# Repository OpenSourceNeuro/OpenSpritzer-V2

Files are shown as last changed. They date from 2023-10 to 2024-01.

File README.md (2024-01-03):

<p align="left">
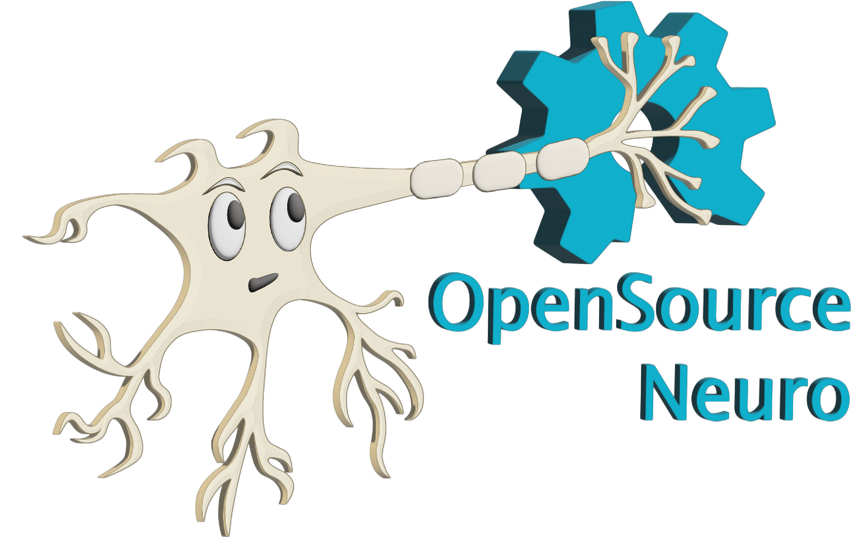
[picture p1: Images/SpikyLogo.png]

</p>

<h1 align="center"> OpenSpritzer v2</h1>
<h3 align="center">  An Open hardware pressure ejection system for reliably delivering picolitre volumes.</h3></p>
<h6 align="right">developed by M.J.Y. Zimmermann</h6>

<br></br>

This project is licensed under the <a href="https://www.gnu.org/licenses/gpl-3.0.html">GNU General Public License v3.0</a>
<br>
The hardware is licensed under the <a href="https://cern-ohl.web.cern.ch">CERN OHL v1.2</a>

***

<div align= "justify">

<p>
Designed for ease of use, robustness and low-cost, the “Openspritzer” is an open hardware “Picospritzer” as routinely used in biological labs around the world. The performance of Openspritzer and commercial alternatives is effectively indistiguishable.
</p>

<p>
The system is based on a solenoid valve connected to a pressure gauge. Control can be attained directly via an external TTL pulse or internally through an Arduino set by a rotary encoder. The basic setup can be put together for ~400€, or substantially less if you are prepare to shop around.
</p>

<p>
We anticipate that due to its high performance and low cost Openspritzer will be of interest to a broad range of researchers working in the life and physical sciences.
</p>

<br>

</div>

<p align="center">
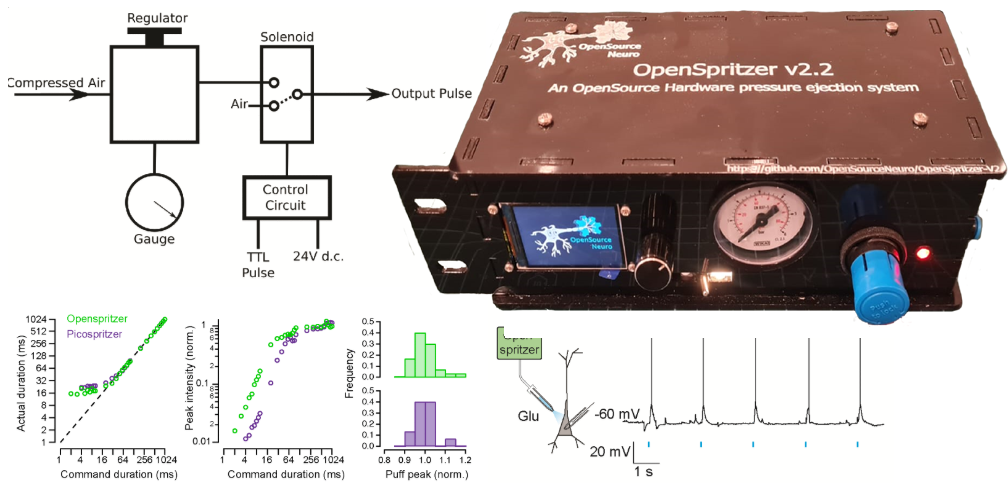
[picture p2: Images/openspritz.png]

</p>

<p align= "right">
The original work was published in <a href="https://www.nature.com/articles/s41598-017-02301-2"> Forman et al. 2017, Scientific Reports</a>
</p>

***

<h2 align="left">
OpenSpritzer, a DIY open source micro-injector:
</h2>

<br>

<div align= "justify">

<p>
Compared to similar commercial systems that can cost up to several thousand pounds, the cost of the fully equipped Openspritzer (~£300) makes it particularly attractive for those wishing to pursue cutting-edge techniques in low resource environments.
</p>

<p>
This repository contains detailed <a href="https://github.com/OpenSourceNeuro/OpenSpritzer-V2/blob/main/Installation_Manual.md">assembly instructions and an operation manual</a> for OpenSpritzer. The <a href="https://github.com/OpenSourceNeuro/OpenSpritzer-V2/blob/main/BOM.csv">bill of material</a> details all pneumatic, mechanical and electronic components required.
</p>

<p>
To simplify the wiring assembly, a customed circuit board has been designed. PCB prototype companies (i.e. <a href="jlcpcb.com"> JLCPCB</a>) will only require the <a href="https://github.com/OpenSourceNeuro/OpenSpritzer-V2/tree/main/PCB_Rack%20version"> gerber.zip</a> folder to be sent to them for production.
</p>

<br></br>

</div>

***

<h2 align="left">
Openspritzer rivals the performance of commercial systems:
</h2>

<br>

<div align= "justify">

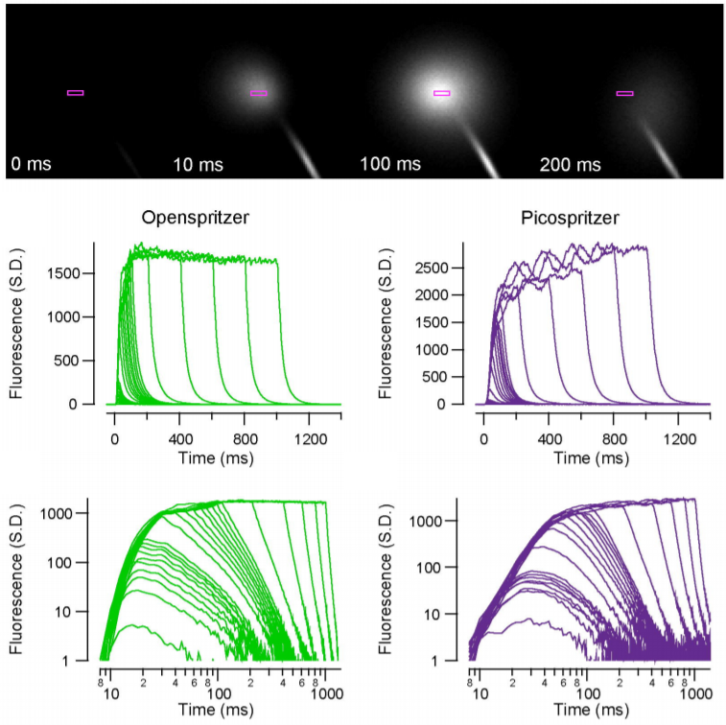
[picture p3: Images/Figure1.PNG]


<p>
Openspritzer control over dose delivery matches that of a leading commercial alternative.
</p>

<p>
To directly assess the time precision and reliability of Openspritzer we visualised fluorescent dye puffs from a sharp microelectrode under two-photon microscopy. The images were taken from a puff with a duration of several seconds using a wide area scan (rectangles).
</p>

<p>
Fluorescence profiles of different command-duration puffs are shown for Openspritzer (green) and Picospritzer, a popular microinjection system(purple), respectively. The same data is shown again in log-log space to highlight details of shorter pulses. Overall, both devices behave in a very similar way in terms of providing effective and near linear control over the total dosage.
</p>

<br></br>

</div>

***

<h2 align="left">
OpenSpritzer in neuroscience experiments:
</h2>

<br>

<div align= "justify">

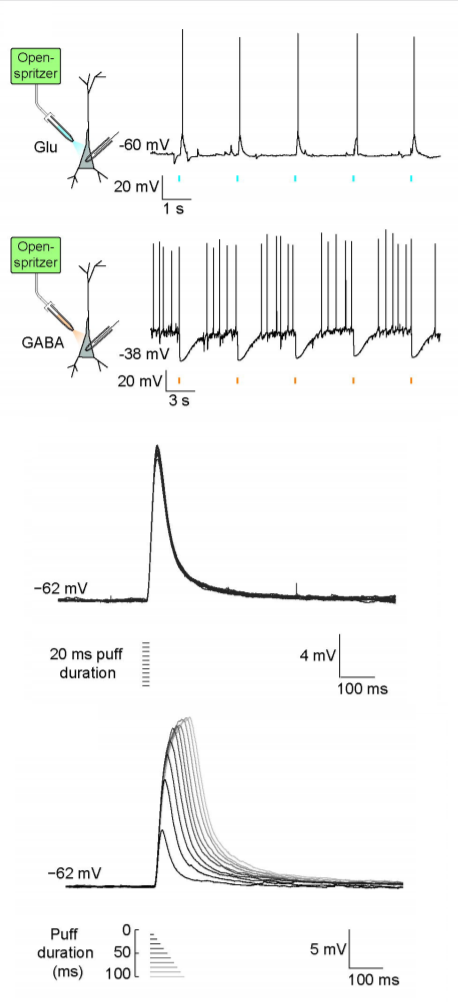
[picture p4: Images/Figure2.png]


<p>
Openspritzer controls neural activity by delivering neurotransmitters with millisecond precision.
</p>

<p>
To demonstrate the utility of Openspritzer, we use it in a series of standard neurobiological applications: We delivered precise amounts of glutamate(cyan) and GABA(orange) to hippocampal neurons to elicit time- and dose-precise excitatory and inhibitory responses respectively, while monitoring the voltage response of the recorded neuron in current-clamp mode.
</p>

<p>
20 ms doses of glutamate (100 μM) reliably evoked excitatory postsynaptic potentials (EPSPs) and action potentials. Similarly, action potential activity elicited via somatic current injection could be suppressed by 20 ms puffs of GABA (100 μM).
</p>

<p>
To assess the accuracy of the drug delivery, we applied 10 sweeps where a 20 ms glutamate puff was applied after 500 ms produced almost identical EPSPs demonstrating the precise timing of Openspritzer and highly conserved puff volumes.
</p>

<p>
Then, to test the effect of command duration on effective dose delivey, we next applied puffs of increasing duration from 10 to 100 ms in 10 ms steps. Here, each additional 10 ms increase in duration produced a clear increase in both EPSP duration and amplitude. These results confirm the reliability and precision of Openspritzer for delivering small doses of an agent to a widely used biological sample in a controlled manner.
</p>

<br></br>

</div>

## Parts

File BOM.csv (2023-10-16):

Name | Manufacturer | Order ID | Retailer | Retailer ID | Quantity |  |  | Observation
Solenoid | FESTO | MHJ10-S-2,5-QS-6-HF | RS | 175-2145 | 1 | https://fr.rs-online.com/web/p/electrodistributeurs/1752145 | 92.35 | Pneumatics
Precision pressure regulator | FESTO | MS2-LR-QS6-D6-A8-B | RS | 204-0052 | 1 | https://fr.rs-online.com/web/p/regulateurs-de-pression/2040052 | 30.38 | Pneumatics
Gauge | WIKA | 30810876 | RS | 222-7480 | 1 | https://fr.rs-online.com/web/p/manometres/2227480 | 11.52 | Pneumatics
6mm air tubing | FESTO | PEN-6XT-NT | RS | 126-2781 | 1 |  |  | Pneumatics
PicoNozzle Kit | World Precision Instrument | 5430 - x | WPI |  | 1 |  |  | Pneumatics
ESP32 -devkit 32 | Espressif | ESP32-DEVKITC-32E | DigiKey | 1965-ESP32-DEVKITC-32E-ND | 1 | https://www.digikey.fr/fr/products/detail/espressif-systems/ESP32-DEVKITC-32E/12091810 | 9.3 | Electronics
2 inch LCD display module ST7789 | Waveshare
PCB socket | Samtec | SSW-116-02-G-S | RS |  | 2 |  |  | Electronics
NPN transistor | onsemi | KSP 2222 ABU | RS | 739-0385 | 3 | https://fr.rs-online.com/web/p/transistors-bipolaires/7390385?gb=s | 3.18 | Electronics
Rotary Encoder |  | KY-040 |  |  | 1 |  | 1.5 | Electronics
Knob for rotary encoder |  |  |  |  | 1 |  |  | Electronics
DPDT switch | nkk switches | B22AH | DigiKey | 360-3752-ND | 1 |  | 6.2 | Electronics
SPST footswitch | RS Pro | 808-6989 | RS | 808-6989 | 1 |  | 33.78 | Electronics
24V DC PSU 2.1 mm jack | RS Pro | 436-058 | RS | 436-058 | 1 |  | 25 | Electronics
2.1 mm right angle DC socket | RS Pro | 884-0957 | RS | 884-0957 | 1 |  | 1.87 | Electronics
24 V Zener Diode | STMicroelectronics | 1N5822 | RS | 687-0877 | 1 |  |  | Electronics
1 kOhm resistor | Digikey | CF14JT1K00CT-ND | Digikey |  | 1 |  |  | Electronics
2 kOhm resistor | Digikey | CF14JT2K00CT-ND | Digikey |  | 1 |  |  | Electronics
220 Ohm resistor | Digikey | CF14JT220RCT-ND | Digikey |  | 3 |  |  | Electronics
Voltage step-down regulator | RS Pro | LM2596T-5.0 NOPB | RS | 533-3743 | 1 |  | 6.62 | Electronics
Capacitor 680 µF | RS Pro | 526-1569 | RS | 526-1569 | 1 |  | 1.06 | Electronics
Capacitor 220 µF | RS Online | 526-1480 | RS | 526-1480 | 1 |  | 0.58 | Electronics
Inductor 33 µH | Wurth Elektronik | 744772330 | RS | 489-0059 | 1 |  |  | Electronics
3 mm LED (white preferably ) | Digikey | 350-1557-ND | Digikey |  | 3 |  |  | Electronics
Mount for 3 mm LED | Digikey | 67-1330-ND | Digikey |  | 1 |  |  | Electronics
BNC coaxial connectors | RS PRO | 546-5115 | RS | 546-5115 | 2 |  |  | Electronics
Cable Mount BNC Connector | RS PRO | 546-3721 | RS | 546-3721 | 1 |  |  | Electronics
2 way JST Female Connector Housing | JST | XHP-2 | RS | 820-1611 | 1 |  |  | Electronics
3 way JST Female Connector Housing | JST | XHP-3 | RS | 820-1614 | 2 |  |  | Electronics
8 way JST Female Connector Housing | JST | XHP-8 | RS | 820-1633 |  |  |  | Electronics
2 way JST PCB header | JST | B2B-XH | RS | 820-1554 | 1 |  |  | Electronics
3 way JST PCB header | JST | B3B-XH | RS | 820-1557 | 2 |  |  | Electronics
8 way JST PCB header | JST | B8B-XH | RS | 820-1576 |  |  |  | Electronics
Rocker LED switch |  | BRockerB-XH | Ebay |  | 1 |  |  | Electronics

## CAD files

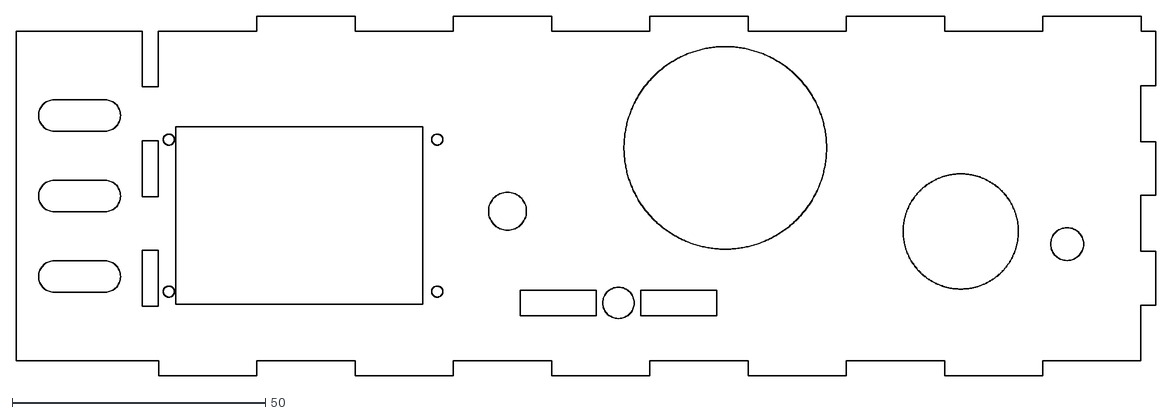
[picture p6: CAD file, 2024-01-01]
Casing/front.dxf
225.0 x 71.0

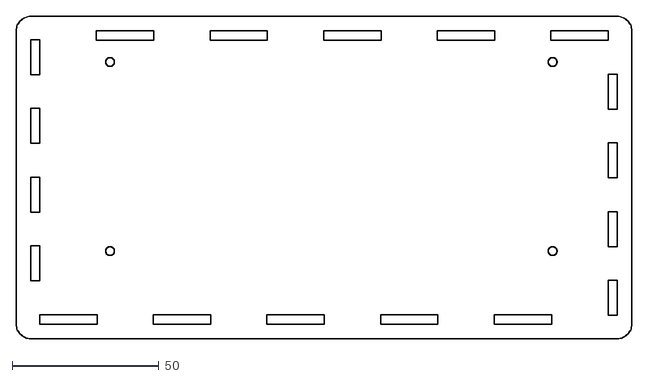
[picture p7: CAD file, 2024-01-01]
Casing/Rack_mount/bottom.dxf
210.0 x 110.0

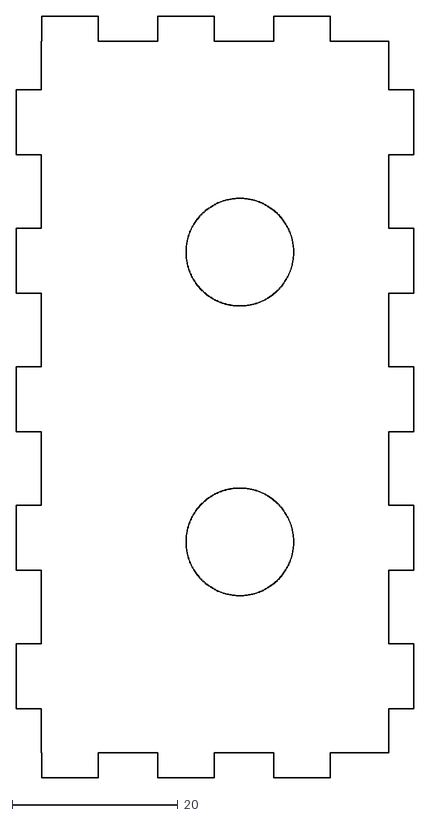
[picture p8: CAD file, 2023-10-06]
Casing/left.dxf
48.0 x 92.0

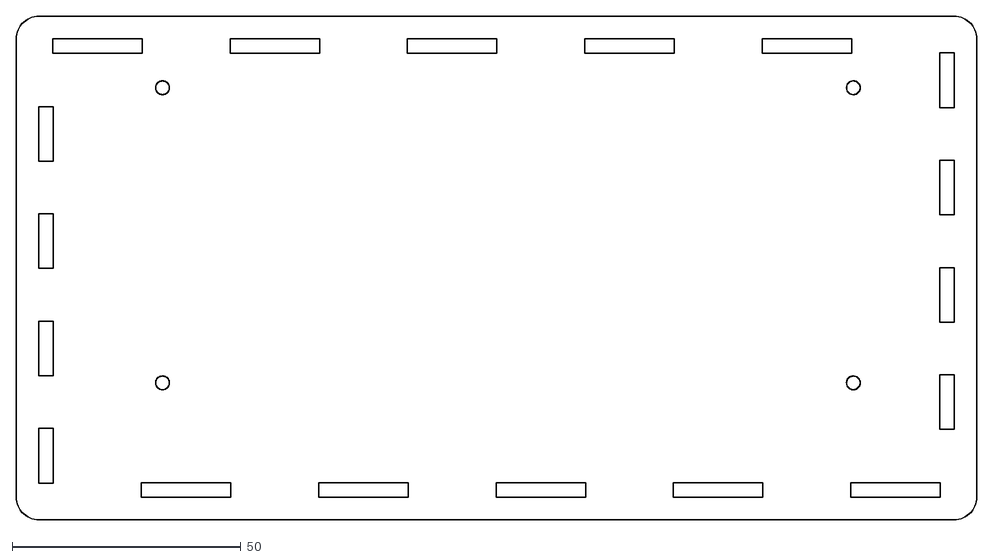
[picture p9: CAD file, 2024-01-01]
Casing/Rack_mount/top.dxf
210.0 x 110.0

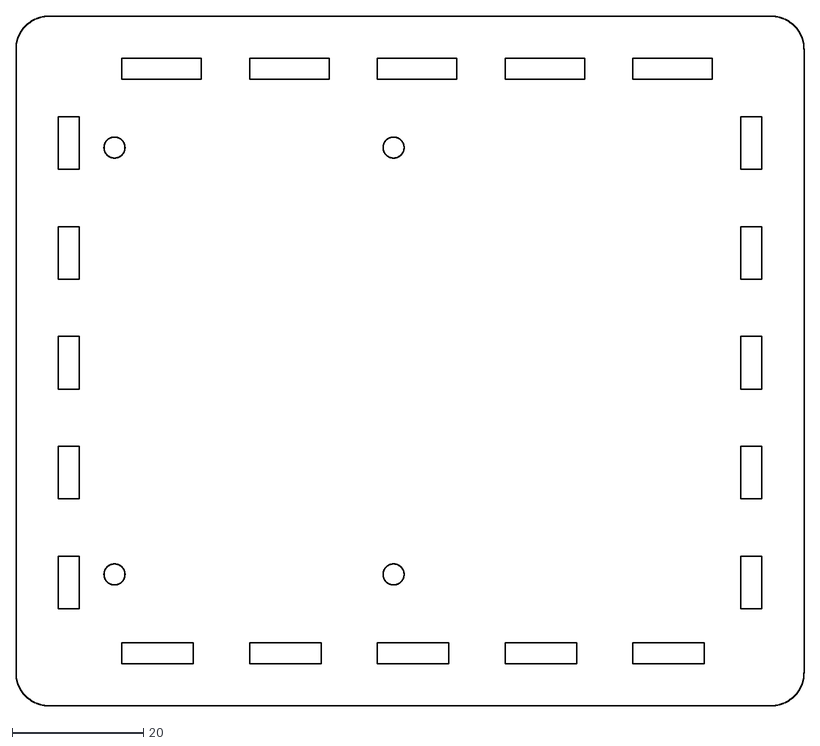
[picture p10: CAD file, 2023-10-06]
Casing/bottom.dxf
120.0 x 105.0

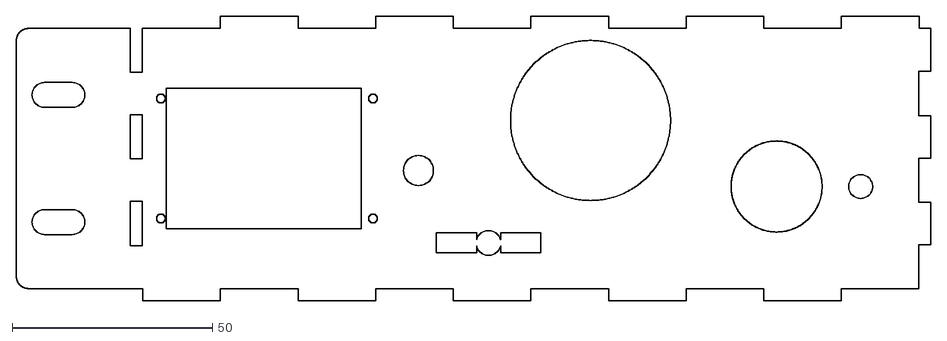
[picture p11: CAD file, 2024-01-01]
Casing/Rack_mount/front.dxf
228.5 x 71.0

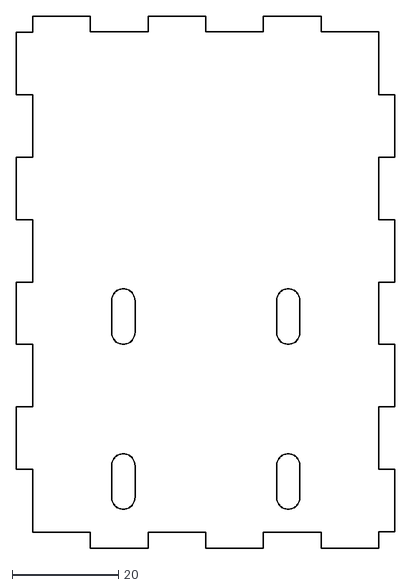
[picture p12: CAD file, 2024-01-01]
Casing/Rack_mount/left.dxf
71.1 x 100.0

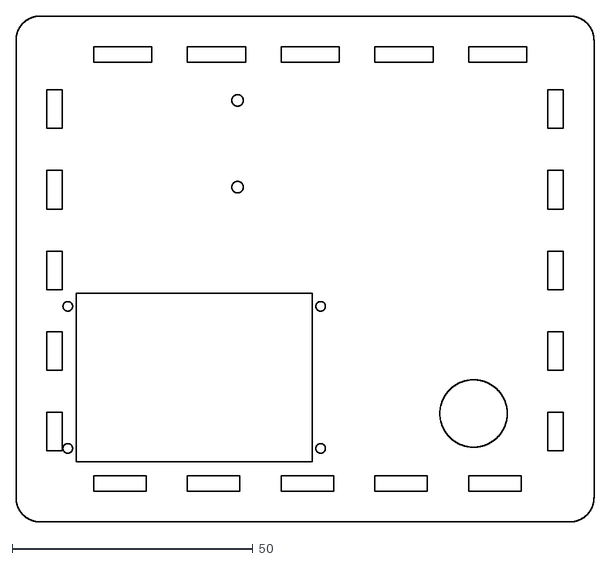
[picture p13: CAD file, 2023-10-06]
Casing/top.dxf
120.0 x 105.0

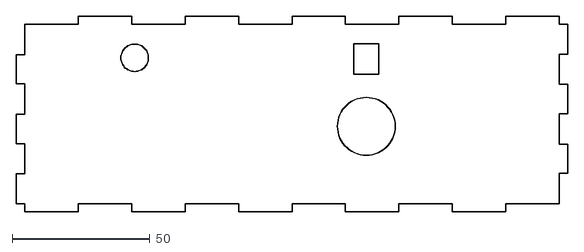
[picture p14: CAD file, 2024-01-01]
Casing/Rack_mount/back.dxf
200.0 x 71.0

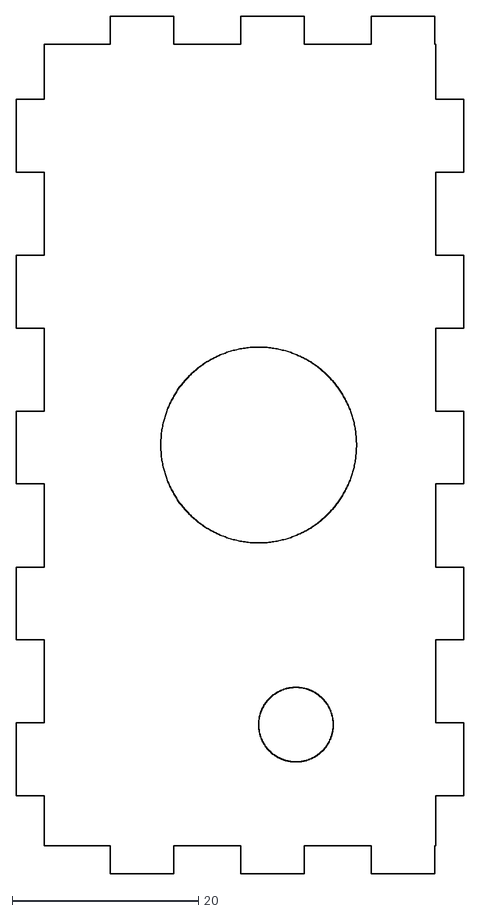
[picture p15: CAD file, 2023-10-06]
Casing/right.dxf
48.0 x 92.0

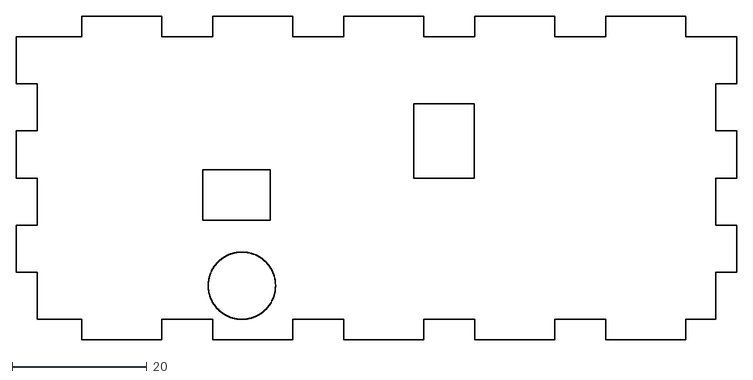
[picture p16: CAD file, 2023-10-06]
Casing/back.dxf
107.0 x 48.0

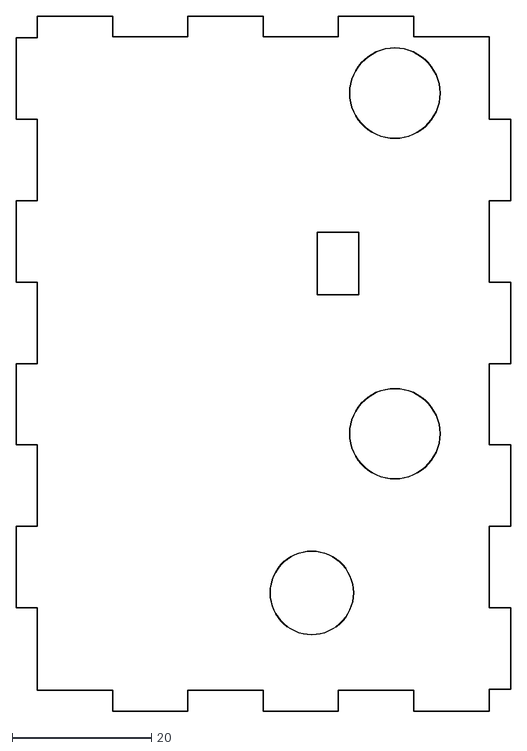
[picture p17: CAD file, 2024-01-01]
Casing/Rack_mount/right.dxf
71.1 x 100.0

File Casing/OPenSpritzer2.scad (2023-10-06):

Acrylic_Wall = 3;
tol = 0.1;
Smoothness = 60;
xxx = 20;


x_PCB = 65;
y_PCB = 85;
z_PCB = 2;
r_PCB = 3;
r_Acrylic = 5;

PCB_Spacing = 2.54;

r_hex = 5.65/2;
hex_bottom = 8;
hex_top = 20+8;



// // // Switches // // //
DXF = 0;

PCB = 1;

BNC90 = 10;
DPDT = 10;
Power = 10;
ESP = 10;
Rotary = 10;

Regulator = 1;
Solenoid = 1;

Hex_Bottom = 1;
Hex_Top = 1;

Acrylic_Bottom  = 1;
Acrylic_Top  = 1;
Acrylic_Front  = 1;
Acrylic_Back  = 1;
Acrylic_Left  = 1;
Acrylic_Right  = 1;

// // // Parameters // // // //

x_BNC90 = 14.8;
y_BNC90 = 14.9;
z_BNC90 = 13.1;
h1_BNC90 = 10.5;
r1_BNC90 = 12.8/2;
h2_BNC90 = 9.8;
r2_BNC90 = 9.6/2;
h_pinBNC90 = 4.2;
r_pinBNC90 = 0.89/2;
offset_pinBNC90 = 0.2;

x_ESP = 55;
y_ESP = 28;
z_ESP = 11.5;
x_USB = 6;
y_USB = 9;
z_USB = 6;
h_USB = 3;
xpos_ESP = 4.3;
ypos_ESP = 0;
r_pinUSB = 0.6/2;
h_pinUSB = 5;

x_Power = 9;
y_Power = 13.6;
z_Power = 11;
xoffset_pinPower1 = 25;
yoffset_pinPower1 = y_PCB - 4.75;
xoffset_pinPower2 = 20.3;
yoffset_pinPower2 = y_PCB - 7.79;
xoffset_pinPower3 = 25;
yoffset_pinPower3 = y_PCB - 10.8;
x_pinPower1 = 4.5;
y_pinPower1 = y_Power-7.5;
x_pinPower2 = -0.1;
y_pinPower2 = y_Power-10.8;
x_pinPower3 = 4.5;
y_pinPower3 = y_Power-13.6;
xpos_Power = 60;
ypos_Power = y_PCB-4.75;

x_Switch = 8.8;
y_Switch = 13.7;
z_Switch = 8.8;
r_Switch = 6/2;
h_Switch = 2.7;
hpos_Switch = 4.4;
xoffset_pinSwitch = 1.86;
yoffset_pinSwitch = 7.62;
h_pinSwitch = 4.2;
r_pinSwitch = 0.6/2;
xoffset_pinSwitch1 = 25;
xoffset_pinSwitch2 = 25+PCB_Spacing;
xoffset_pinSwitch3 = 25-PCB_Spacing;
xoffset_pinSwitch4 = 50;
xoffset_pinSwitch5 = 50+PCB_Spacing;
xoffset_pinSwitch6 = 50-PCB_Spacing;
yoffset_pinSwitch1 = y_PCB-88.07;
yoffset_pinSwitch2 = y_PCB-90.62;

xpos1_M3 = 5;
xpos2_M3 = 47.5;
ypos1_M3 = 10;
ypos2_M3 = 75;
r_M3 = 3/2;

r_Hole = 0.5+tol;
ypos_BNC90_1 = y_PCB-60;
ypos_BNC90_1bis = y_PCB-82.54;
ypos_BNC90_2 = y_PCB-25;
ypos_BNC90_2bis = y_PCB-22.5;
xpos_BNC90 = 12.4;
xpos_Switch_1 = 24;
xpos_Switch_1bis = 27.7;
ypos_Switch = y_PCB-80.75;

xpos_Rotary = 47.5;
ypos_Rotary = 1.5;
zpos_Rotary = 22;
r_Rotary = 7.5/2;
h_Rotary = 25;

xmargin_Acrylic = 10;
ymargin_Acrylic = 10;
x_Acrylic = x_PCB + 2*xmargin_Acrylic;
y_Acrylic = y_PCB + 2*ymargin_Acrylic;
z_Acrylic = Acrylic_Wall;

x_AcrylicFront = x_PCB;
y_AcrylicFront = Acrylic_Wall;
z_AcrylicFront = z_PCB + hex_bottom + hex_top ;

x_AcrylicSide = Acrylic_Wall;
y_AcrylicSide = y_PCB;
z_AcrylicSide = z_PCB + hex_bottom + hex_top;

y1margin_AcrylicFront = 2;
y2margin_AcrylicFront = 2;

x1margin_AcrylicSide = 2;
x2margin_AcrylicSide = 2;
x1margin_AcrylicFront = x1margin_AcrylicSide+Acrylic_Wall;
x2margin_AcrylicFront = x2margin_AcrylicSide+Acrylic_Wall;

y1margin_AcrylicSide = y1margin_AcrylicFront;
y2margin_AcrylicSide = y2margin_AcrylicFront;




// // // Functions // // //

if (PCB == 1){
    difference(){
        PCB();
        translate([xpos1_M3,ypos1_M3,-tol])cylinder(r=r_M3,h=z_PCB+2*tol,$fn=Smoothness);
        translate([xpos1_M3,ypos2_M3,-tol])cylinder(r=r_M3,h=z_PCB+2*tol,$fn=Smoothness);
        translate([xpos2_M3,ypos1_M3,-tol])cylinder(r=r_M3,h=z_PCB+2*tol,$fn=Smoothness);
        translate([xpos2_M3,ypos2_M3,-tol])cylinder(r=r_M3,h=z_PCB+2*tol,$fn=Smoothness);
    }
}

if (Rotary == 1){
    Rotary();
}


module Rotary(){
    translate([xpos_Rotary,ypos_Rotary,zpos_Rotary])rotate([90,0,0])cylinder(r=r_Rotary,h=h_Rotary,$fn=Smoothness);
}

if (BNC90 == 1){
    translate([xpos_BNC90,ypos_BNC90_1,0])BNC90();
    translate([xpos_BNC90,ypos_BNC90_2,0])BNC90();
}

if (ESP == 1){
    translate([14.8,y_PCB-0.25,z_PCB])rotate([0,0,-90])ESP();
}

if (Power == 1){
    translate([xpos_Power,ypos_Power,0])Power();
}

if (DPDT == 1){
    translate([xpos_Switch_1,ypos_Switch,0])Switch();
}

if (Hex_Bottom == 1){
    translate([xpos1_M3,ypos1_M3,-hex_bottom])Hex(hex_bottom);
    translate([xpos2_M3,ypos1_M3,-hex_bottom])Hex(hex_bottom);
    translate([xpos1_M3,ypos2_M3,-hex_bottom])Hex(hex_bottom);
    translate([xpos2_M3,ypos2_M3,-hex_bottom])Hex(hex_bottom);
}

if (Hex_Top == 1){
    translate([xpos1_M3,ypos1_M3,z_PCB])Hex(hex_top);
    translate([xpos2_M3,ypos1_M3,z_PCB])Hex(hex_top);
    translate([xpos1_M3,ypos2_M3,z_PCB])Hex(hex_top);
    translate([xpos2_M3,ypos2_M3,z_PCB])Hex(hex_top);
}

if (Regulator == 1){
    translate([90,28,15])rotate([0,0,0])Regulator();
}

if (Solenoid == 1){
    translate([52.5,y_PCB-30,z_PCB+hex_top-10-tol])rotate([0,0,0])Solenoid();
}

if (Acrylic_Bottom == 1 && DXF == 0){
    Acrylic_Botom();
}
if (Acrylic_Bottom == 1 && DXF == 1){
    Acrylic_Botom_DXF();
}


if (Acrylic_Top == 1 && DXF == 0){
    Acrylic_Top();
}
if (Acrylic_Top == 1 && DXF == 1){
    Acrylic_Top_DXF();
}


if (Acrylic_Front == 1 && DXF == 0){
    Acrylic_Front();
}
if (Acrylic_Front == 1 && DXF == 1){
    Acrylic_Front_DXF();
}


if (Acrylic_Back == 1 && DXF == 0){
    Acrylic_Back();
}
if (Acrylic_Back == 1 && DXF == 1){
    Acrylic_Back_DXF();
}


if (Acrylic_Left == 1 && DXF == 0){
    Acrylic_Left();
}
if (Acrylic_Left == 1 && DXF == 1){
    Acrylic_Left_DXF();
}


if (Acrylic_Right == 1 && DXF == 0){
    Acrylic_Right();
}
if (Acrylic_Right == 1 && DXF == 1){
    Acrylic_Right_DXF();
}


// // // Modules // // //


module PCB(){
    color([0.1,0.8,0])translate([r_PCB,r_PCB,0])minkowski(){
        cube([x_PCB-2*r_PCB,y_PCB-2*r_PCB,z_PCB-tol]);
        cylinder(r=r_PCB,h=tol,$fn=Smoothness);
    }
}

module BNC90(){
    color([1,1,1])translate([-x_BNC90+offset_pinBNC90+r_pinBNC90,-y_BNC90/2,z_PCB])cube([x_BNC90,y_BNC90,z_BNC90]);
    color([1,1,1])translate([-x_BNC90+offset_pinBNC90+r_pinBNC90-h1_BNC90,0,z_BNC90/2+z_PCB])rotate([0,90,0])cylinder(r=r1_BNC90+tol,h=h1_BNC90,$fn=Smoothness);
    color([192/255,192/255,192/255])translate([-x_BNC90+offset_pinBNC90+r_pinBNC90-h1_BNC90-h2_BNC90,0,z_BNC90/2+z_PCB])rotate([0,90,0])cylinder(r=r2_BNC90,h=h2_BNC90,$fn=Smoothness);
    translate([0,0,-h_pinBNC90+z_PCB])cylinder(r=r_pinBNC90,h=h_pinBNC90,$fn=Smoothness);
    translate([0,-PCB_Spacing,-h_pinBNC90+z_PCB])cylinder(r=r_pinBNC90,h=h_pinBNC90,$fn=Smoothness);
}

module Power(){
    color([0.1,0.1,0.1])translate([-x_pinPower1,-y_pinPower1,z_PCB]){
        cube([x_Power,y_Power+xxx,z_Power]);
        translate([x_pinPower1,y_pinPower1,-tol-z_PCB])cylinder(r=r_Hole,h=z_PCB+2*tol,$fn=Smoothness);
        translate([x_pinPower2,y_pinPower2,-tol-z_PCB])cylinder(r=r_Hole,h=z_PCB+2*tol,$fn=Smoothness);
        translate([x_pinPower3,y_pinPower3,-tol-z_PCB])cylinder(r=r_Hole,h=z_PCB+2*tol,$fn=Smoothness);
    }
}

module Switch(){
    translate([-xoffset_pinSwitch,-y_Switch+yoffset_pinSwitch,z_PCB]){
        color([0.8,0.1,0.1])cube([x_Switch,y_Switch,z_Switch]);
        color([192/255,192/255,192/255])translate([x_Switch/2,0,hpos_Switch])rotate([90,0,0])cylinder(r=r_Switch+tol,h=h_Switch+xxx,$fn=Smoothness);
        translate([xoffset_pinSwitch,y_Switch-yoffset_pinSwitch,-h_pinSwitch+z_PCB])cylinder(r=r_pinSwitch,h=h_pinSwitch,$fn=Smoothness);
        translate([x_Switch-xoffset_pinSwitch,y_Switch-yoffset_pinSwitch,-h_pinSwitch+z_PCB])cylinder(r=r_pinSwitch,h=h_pinSwitch,$fn=Smoothness);
        translate([xoffset_pinSwitch,y_Switch-yoffset_pinSwitch+2*PCB_Spacing,-h_pinSwitch+z_PCB])cylinder(r=r_pinSwitch,h=h_pinSwitch,$fn=Smoothness);
        translate([xoffset_pinSwitch+PCB_Spacing,y_Switch-yoffset_pinSwitch+2*PCB_Spacing,-h_pinSwitch+z_PCB])cylinder(r=r_pinSwitch,h=h_pinSwitch,$fn=Smoothness);
        translate([xoffset_pinSwitch+2*PCB_Spacing,y_Switch-yoffset_pinSwitch+2*PCB_Spacing,-h_pinSwitch+z_PCB])cylinder(r=r_pinSwitch,h=h_pinSwitch,$fn=Smoothness);
        translate([xoffset_pinSwitch,y_Switch-yoffset_pinSwitch+3*PCB_Spacing,-h_pinSwitch+z_PCB])cylinder(r=r_pinSwitch,h=h_pinSwitch,$fn=Smoothness);
        translate([xoffset_pinSwitch+PCB_Spacing,y_Switch-yoffset_pinSwitch+3*PCB_Spacing,-h_pinSwitch+z_PCB])cylinder(r=r_pinSwitch,h=h_pinSwitch,$fn=Smoothness);
        translate([xoffset_pinSwitch+2*PCB_Spacing,y_Switch-yoffset_pinSwitch+3*PCB_Spacing,-h_pinSwitch+z_PCB])cylinder(r=r_pinSwitch,h=h_pinSwitch,$fn=Smoothness);
    }
}

module Hex(height){
    color([255/255,215/255,0])cylinder(r=r_hex,h=height,$fn=8);
}

module ESP(){
    translate([-xpos_ESP,ypos_ESP,z_PCB]){cube([x_ESP,y_ESP,z_ESP]);
        translate([-xxx,y_ESP/2-y_USB/2,z_ESP+h_USB-z_USB/2])cube([x_USB+xxx,y_USB,z_USB]);
    }  
}
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

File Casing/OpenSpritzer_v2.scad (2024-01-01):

Wall = 3;
tol = 0.1;
Smoothness = 360;
Sm = 60;
Acrylic = [0,0,0.8,0.8];

// // // // // // // // // // // // // //
// // // // //   Switches  // // // // //

DXF = 1;

PCB = 10;
BNC90 = 10;
DPDT = 10;
Power = 10;
Power_Switch = 10;
ESP = 10;
Rotary = 10;
Festo = 10;

Regulator = 10;
Manometer = 10;
Solenoid = 10;
Screen = 10;

Hex_Bottom = 10;
Hex_Top = 10;

Rack19 = 10;

Acrylic_Bottom  = 10;
Acrylic_Top  = 10;
Acrylic_Front  = 10;
Acrylic_Back  = 10;
Acrylic_Left  = 1;
Acrylic_Right  = 10;


// // // // // // // // // // // // // //
// // // // General Settings  // // // //

r_hex = 5.65/2;
hex_bottom = 5;
hex_top = 18+20+20;
z_PCB = 2;

x_Box = 200;
y_Box = 100;
z_Box = hex_bottom + z_PCB + hex_top;
r_Box = 5;

x_PCB = 180;
y_PCB = y_Box-2*Wall-2*tol;
r_PCB = 3;

r_Rack = 3+tol;
x_Rack = 25.5;
x_rack = 7;
x_rack_minus = 5-1;
x_rack_plus = x_rack+x_rack_minus;
d_Rack = 15.9;


xpos1_M3 = x_Box-Wall-x_PCB+10;
xpos2_M3 = x_Box-Wall-x_PCB+161;
ypos1_M3 = y_Box-Wall-tol-72;
ypos2_M3 = y_Box-Wall-tol-7.5;
r_M3 = 3/2;




    x_Rack19 = 25;
    y_Rack19 = 2;
    z_Rack19 = 44.45;
    
    X_Rack19 = 2;
    Y_Rack19 = 45;
    Z_Rack19 = 44.45;
    
    d_Rack19 = 13;
    D_Rack19 = 31;
    l_Rack19 = 14.5;
    r_Rack19 = 4/2+0.2;
    R_Rack19 = 7/2;
    L_Rack19 = 6;
    dd_Rack19 = 25+2*R_Rack19;
    ypos1 = 8;
    ypos2 = 17;
    ypos3 = 30;
    ypos4 = 39;
    xpos1 = 6;
    xpos2 = 12;

// // // // // // // // // // // // // //
// // // // //  Functions  // // // // //

if (PCB == 1){
    translate([x_Box-x_PCB-Wall-tol,Wall+tol,Wall+hex_bottom])difference(){
        PCB();
        translate([32,y_PCB-7.1,-20])cylinder(r=1.3,h=100,$fn=60);
        translate([32,y_PCB-25.1,-20])cylinder(r=1.3,h=100,$fn=60);
    }
}




if (BNC90 == 1){
    BNC90();
}

if (ESP == 1){
    ESP();
}

if (Power == 1){
    Power();
}

if (Power_Switch == 1){
    Power_Switch();
}

if (DPDT == 1){
    Switch();
}

if (Hex_Bottom == 1){
    translate([xpos1_M3,ypos1_M3,Wall])Hex(hex_bottom);
    translate([xpos2_M3,ypos1_M3,Wall])Hex(hex_bottom);
    translate([xpos1_M3,ypos2_M3,Wall])Hex(hex_bottom);
    translate([xpos2_M3,ypos2_M3,Wall])Hex(hex_bottom);
}

if (Hex_Top == 1){
    translate([xpos1_M3,ypos1_M3,Wall+hex_bottom+z_PCB])Hex(hex_top);
    translate([xpos2_M3,ypos1_M3,Wall+hex_bottom+z_PCB])Hex(hex_top);
    translate([xpos1_M3,ypos2_M3,Wall+hex_bottom+z_PCB])Hex(hex_top);
    translate([xpos2_M3,ypos2_M3,Wall+hex_bottom+z_PCB])Hex(hex_top);
}

if (Festo == 1){
    Festo();
}
if (Regulator == 1){
    Regulator();
}
if (Manometer == 1){
    Manometer();
}

if (Solenoid == 1){
    Solenoid();
}

if (Screen == 1){
    Screen();
}
if (Rotary == 1){
    Rotary();
}
if  (Rack19 == 1){
    Rack19();
}


if (Acrylic_Bottom == 1 && DXF == 0){
    Acrylic_Botom();
}
if (Acrylic_Bottom == 1 && DXF == 1){
    Acrylic_Botom_DXF();
}


if (Acrylic_Top == 1 && DXF == 0){
    Acrylic_Top();
}
if (Acrylic_Top == 1 && DXF == 1){
    Acrylic_Top_DXF();
}


if (Acrylic_Front == 1 && DXF == 0){
    Acrylic_Front();
}
if (Acrylic_Front == 1 && DXF == 1){
    Acrylic_Front_DXF();
}


if (Acrylic_Back == 1 && DXF == 0){
    Acrylic_Back();
}
if (Acrylic_Back == 1 && DXF == 1){
    Acrylic_Back_DXF();
}


if (Acrylic_Left == 1 && DXF == 0){
    Acrylic_Left();
}
if (Acrylic_Left == 1 && DXF == 1){
    Acrylic_Left_DXF();
}


if (Acrylic_Right == 1 && DXF == 0){
    Acrylic_Right();
}
if (Acrylic_Right == 1 && DXF == 1){
    Acrylic_Right_DXF();
}


// // // // // // // // // // // // // //
// // // // //   Modules   // // // // //

module PCB(){
    color([0.1,0.8,0])translate([r_PCB,r_PCB,0])minkowski(){
        cube([x_PCB-2*r_PCB,y_PCB-2*r_PCB,z_PCB-tol]);
        cylinder(r=r_PCB,h=tol,$fn=Smoothness);
    }
}

module Rotary(){
r_Rotary = 7.5/2;
h_Rotary = 25;
x_Rotary = 19;
y_Rotary = 26;
z_Rotary = 1;
    translate([x_Box-x_PCB-Wall+55,12.5,Wall+hex_bottom+z_PCB+22.5])rotate([90,0,0]){
        cylinder(r=r_Rotary,h=h_Rotary,$fn=Sm);
        translate([-11.25,-y_Rotary+10,0])cube([x_Rotary,y_Rotary,z_Rotary]);
    }
}



module BNC90(){
x_BNC90 = 14.8;
y_BNC90 = 14.9;
z_BNC90 = 13.1;
h1_BNC90 = 10.5;
r1_BNC90 = 12.8/2;
h2_BNC90 = 9.8;
r2_BNC90 = 9.6/2;
h_pinBNC90 = 4.2;
r_pinBNC90 = 0.89/2;
offset_pinBNC90 = 0.2;
    translate([x_Box-Wall-14,Wall+tol+y_PCB-57,Wall+hex_bottom])rotate([0,0,180])BNC();
    translate([x_Box-Wall-14,Wall+tol+y_PCB-8   ,Wall+hex_bottom])rotate([0,0,180])BNC();
    
    module BNC(){
        color([1,1,1])translate([-x_BNC90+offset_pinBNC90+r_pinBNC90,-y_BNC90/2,z_PCB])cube([x_BNC90,y_BNC90,z_BNC90]);
        color([1,1,1])translate([-x_BNC90+offset_pinBNC90+r_pinBNC90-h1_BNC90,0,z_BNC90/2+z_PCB])rotate([0,90,0])cylinder(r=r1_BNC90+tol,h=h1_BNC90,$fn=Sm);
        color([192/255,192/255,192/255])translate([-x_BNC90+offset_pinBNC90+r_pinBNC90-h1_BNC90-h2_BNC90,0,z_BNC90/2+z_PCB])rotate([0,90,0])cylinder(r=r2_BNC90,h=h2_BNC90,$fn=Sm);
        translate([0,0,-h_pinBNC90+z_PCB])cylinder(r=r_pinBNC90,h=h_pinBNC90,$fn=Sm);
        translate([0,-2.54,-h_pinBNC90+z_PCB])cylinder(r=r_pinBNC90,h=h_pinBNC90,$fn=Sm);
    }
}

module Power(){
x_Power = 9;
y_Power = 13.6;
z_Power = 11;
 
    color([0.1,0.1,0.1])translate([x_Box-x_PCB-Wall+110,y_Box-13,Wall+hex_bottom+z_PCB]){
        translate([-x_Power/2,0,0])cube([x_Power,y_Power,z_Power]);
    }
}

module Power_Switch(){
x_Power = 9;
y_Power = 13.6;
z_Power = 11;
r_Power = 21/2;

    
    color([0.1,0.1,0.1])translate([x_Box-x_PCB-Wall+110+x_Power/2,y_Box-Wall-tol,Wall+hex_bottom+z_PCB]){
        translate([-x_Power/2,0,30])rotate([-90,0,0])cylinder(r=r_Power, h=Wall+2*tol, $fn=Sm);
    }
}

module Switch(){
x_Switch = 8.8;
y_Switch = 13.7;
z_Switch = 8.8;
r_Switch = 6/2;
h_Switch = 2.7+5;    
hpos_Switch = 4.4;
    translate([x_Box-x_PCB-Wall+72.5,Wall+tol,Wall+hex_bottom+z_PCB]){
        color([0.8,0.1,0.1])cube([x_Switch,y_Switch,z_Switch]);
        color([192/255,192/255,192/255])translate([0,0,hpos_Switch])rotate([90,0,0])cylinder(r=r_Switch+tol,h=h_Switch,$fn=Sm);
    }
}

module Panels(){
x_Panel = 10;
z_Panel = 5;
r_Switch = 6/2;
hpos_Panel = 4.4-z_Panel/2;

    translate([x_Box-x_PCB-Wall+72.5+r_Switch,-tol,Wall+hex_bottom+z_PCB+hpos_Panel])cube([x_Panel, Wall+2*tol,z_Panel]);
    translate([x_Box-x_PCB-Wall+72.5-x_Panel-r_Switch,-tol,Wall+hex_bottom+z_PCB+hpos_Panel])cube([x_Panel, Wall+2*tol,z_Panel]);
}

module Hex(height){
    color([255/255,215/255,0])cylinder(r=r_hex,h=height,$fn=8);
}

module ESP(){
x_ESP = 55;
y_ESP = 28;
z_ESP = 11.5;
x_USB = 6;
y_USB = 9;
z_USB = 6;
h_USB = 3;
xpos_ESP = 4.3;
ypos_ESP = 0;
r_pinUSB = 0.6/2;
h_pinUSB = 5;
    translate([x_Box-Wall-tol-3.25,14+Wall+tol+y_PCB-32.5,Wall+hex_bottom+z_PCB-1.75])rotate([0,0,180]){
        translate([-xpos_ESP,ypos_ESP,z_PCB]){
            cube([x_ESP,y_ESP,z_ESP]);
            translate([-Wall-tol,y_ESP/2-y_USB/2,z_ESP+h_USB-z_USB/2])cube([x_USB+Wall+tol,y_USB,z_USB]);
        }  
    }
}

module Festo(){
    color([1,0,1])translate([x_Box-12.5,17,Wall+hex_bottom+Wall+17.5])rotate([0,90,0])cylinder(r=12/2,h=25,$fn=Sm);
}

module Regulator(){
    reg_r_base = 27/2;
    reg_h_base = 6.5;
    reg_x = 27;
    reg_y = 25;
    reg_z = 22;
    reg_r_top = 26/2;
    reg_h_top = 3;
    reg_thread_r = 22.75/2;
    reg_thread_h = 7;
    reg_ring_r = 21.5/2;
    reg_ring_h = 4;
    reg_gauge_r = 14/2;
    reg_gauge_h = 2;
    reg_gauge2_h = 5.5;
    reg_gauge2_x = 14+1.1;
    reg_gauge2_z = 5;
    reg_tube_r = 6/2+1;
    reg_tube_h = 50;
    reg_gauge_screw = 22.5/2;
    translate([x_Box-38.5,31.5+Wall,Wall+hex_bottom+Wall+17.5])color([1,0,1])rotate([90,0,0]){
        cylinder(r=reg_r_base,reg_h_base,$fn=Smoothness);
        translate([-reg_x/2,-reg_y/2,reg_h_base])cube([reg_x,reg_y,reg_z]); 
        translate([0,0,reg_h_base+reg_z])cylinder(r=reg_r_top,reg_h_top,$fn=Smoothness);
        translate([0,0,reg_h_base+reg_z+reg_h_top])cylinder(r=reg_thread_r,reg_thread_h,$fn=Smoothness);
        translate([0,0,reg_h_base+reg_z+reg_h_top+reg_thread_h])cylinder(r=reg_ring_r,reg_ring_h,$fn=Smoothness);
        translate([0,-reg_y/2,reg_h_base+reg_z/2])rotate([90,0,0])cylinder(r=reg_gauge_r,h=reg_gauge_h,$fn=Smoothness);
        translate([0,reg_y/2+reg_gauge_h,reg_h_base+reg_z/2])rotate([90,0,0])cylinder(r=reg_gauge_r,h=reg_gauge_h,$fn=Smoothness);
        
        translate([-reg_x/2,0,reg_h_base+reg_z/2])rotate([0,90,0])cylinder(r=reg_tube_r,h=reg_tube_h,$fn=Smoothness);
        translate([reg_y/2,0,reg_h_base+reg_z/2])rotate([0,-90,0])cylinder(r=reg_tube_r,h=reg_tube_h,$fn=Smoothness);        
    }
}  

module Spritzer_LED(){
r_LED = 6/2;
    
    translate([x_Box-17.5,-tol,Wall+hex_bottom+Wall+17.5])rotate([-90,0,0])cylinder(r=r_LED,h=Wall+2*tol,$fn=Sm);
}
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

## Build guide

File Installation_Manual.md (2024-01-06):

<p align="left">

</p>

<h1 align="center"> OpenSpritzer v2 - Installation Manual</h1></p>

<br></br>

<h2 align="left">
Overview
</h2>

<br>

<div align= "justify">

<p>
This document contains detailed assembly instructions, a software guideline and includes a parts list.
</p>

<p>
The Arduino code and 3D casing files (SCAD) for either 3D printing or laser cutting (STL and DXF) can be downloaded <a href="https://github.com/OpenSourceNeuro/OpenSpritzer-V2/tree/main/Casing"><strong>here</strong></a>, and further modified to fit customise purposes. The device is designed to regulate the pressure and duration of a single or repeated puff(s) of compressed air. Typically, the output air port is connected to a glass puffer pipette which has been drawn into a sharp point with a narrow (2-3μm) diameter pore.
</p>

<p>
The device itself consists of a printed circuit board, a microcontroller, a solenoid valve, a pressure regulator with a manometer and various interface, off-the-shelf, components.
</p>

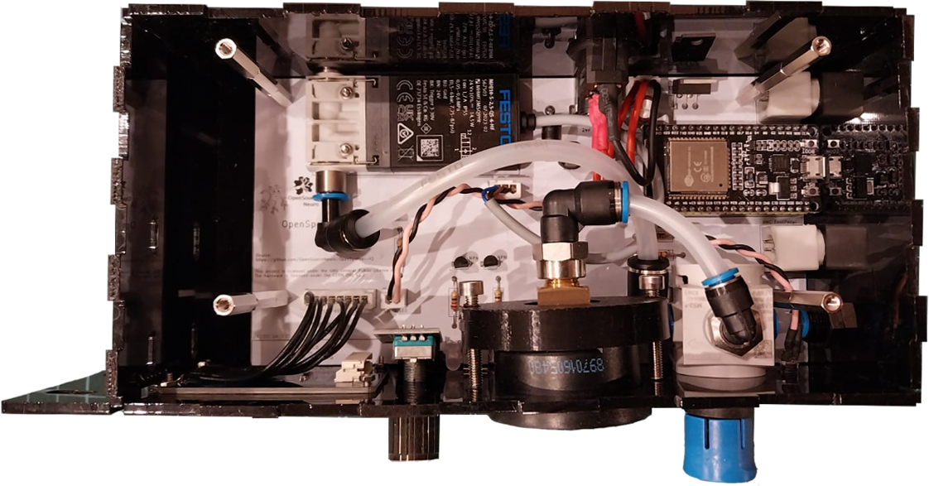
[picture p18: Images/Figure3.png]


<p>
The device is here shown without its covering lid.
The pressure regulator is mounted on the right and attached to the front panel via a retaining threaded ring that comes with the regulator.
M3 threaded spacers are mounted onto the PCB and are meant to be screwed to the top and bottom part of the box.
The solenoid is screwed directly onto the PCB.
The manometer is locked onto the front panel with a 3D printed part and two M3 bolts.
</p>

</div>

<br></br>

## Driver Installation
<br>

OpenSpritzer firmware runs on an Espressif ESP32 board and requires the USB to UART bridge <a href="https://www.silabs.com/developers/usb-to-uart-bridge-vcp-drivers"> CP210x driver</a>,  which can be downloaded<a href="https://www.silabs.com/developers/usb-to-uart-bridge-vcp-drivers?tab=downloads"> <strong>here</strong></a>.

Once the driver has been installed, users can upload and modify the <a href="https://github.com/OpenSourceNeuro/OpenSpritzer-V2/tree/main/Arduino/OpenSpritzer_V2">microcontroller code</a> through the <a href="https://www.arduino.cc/en/software">Arduino IDE</a> (Integrated Development Environment).

<br></br>

## Microcontroller Arduino code

<br>

##### Arduino IDE

<br>

The ESP32 microcontroller runs a C++ code which can be accessed via the Arduino IDE, which can be downloaded <a href="https://www.arduino.cc/en/software">here</a>.

<br>

##### ESP32 Add-on

<br>

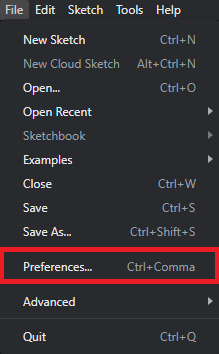
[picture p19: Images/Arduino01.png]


Once the IDE is installed, users needs to install the ESP32 board library:

In the Arduino IDE, go to <strong> File > Preferences </strong>

Enter the following link into the <strong>Additional Board Manager URLs</strong> field:

https://raw.githubusercontent.com/espressif/arduino-esp32/gh-pages/package_esp32_index.json

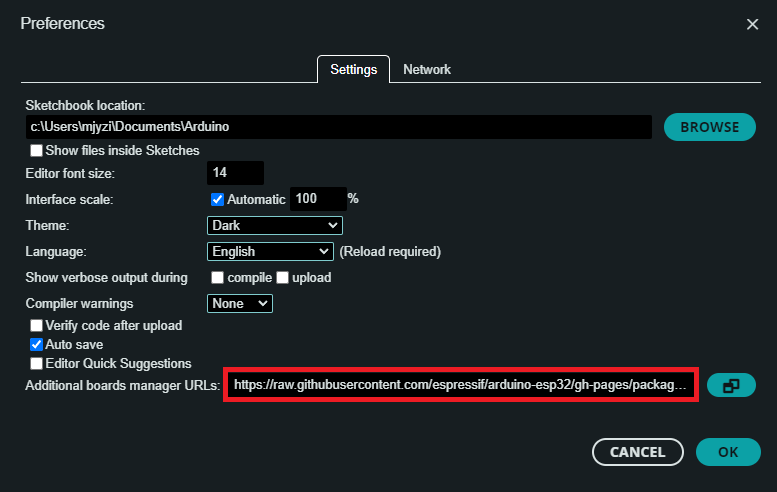
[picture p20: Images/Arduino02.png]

Then click on the <strong>OK</strong> button.

<br></br>

Next, open the Boards Manager. Go to <strong> Tools > Board > Board Manager...</strong>

Search for ESP32 and press install button for the <strong>ESP32 by Espressif Systems</strong>.

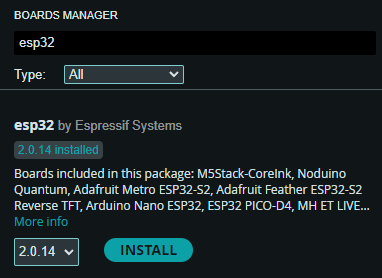
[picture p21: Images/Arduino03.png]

Then click on the <strong>Install</strong> button.

<br></br>

##### Compiling the code

<br>

Within the Arduino IDE, user needs to select the FQBN (Fully Qualified Board Name) on which the code will be compiled for.

Here the ESP32 Dev Module needs to be selected.

Go to <strong>Tools > Board > esp32 > ESP32 Dev Module </strong>


The board name should be displayed  as shown.

<br></br>

Before compiling the LED Zappelin code, a few librairies need to be installed:
  - Arduino-SerialCommand
  - Adafruit_TLC5947
  - Adafruit_NeoPixel

Most of them can be downloaded from the Arduino IDE: Go to <strong>Sketch > Include Librairy > Manage Libraries</strong>, enter the library name, then install it following the same process as for the board library.

We however recommend for the Arduino-SerialCommand library to manually place the library folder which can be found <a href="https://github.com/OpenSourceNeuro/LED-Zappelin-V2/tree/main/Arduino/Librairies">here</a> into the library folder. For Windows Users: <strong>C:/Users/x/Documents/Arduino/libraries</strong>

Now everything is set to compile and verify the code.

Users can now select the COM port on which the ESP32 is connected ( Go to <strong>Tools > port</strong> ) and upload the code onto the board.

<br></br>

##### Code and calibration

<br>

The code runs continuously on the board in a loop detailed in the main tab (LED_Zappelin_V2.ino).
To not interfere with the proper function and communication of the program, avoid modifying this part of the code.

<br>

In <strong>General_Settings.h</strong>:

- There exists two versions for the NeoPixel strips that serve as proxy LEDs for the device. If the proxy LEDs do not display the appropriate colours, comment/uncomment the Adafruit_NeoPixel functions:


<br>

In <strong> LED_Values.h </strong>

- Users can select here the colours displayed by the proxy LEDs by entering the wavelength corresponding to each stimulating LEDs.


- The TLC5947 is a linear current-sink LED driver with a 12bits resolution (4096 values).
However, some LEDs may reach their maximum intensities before reaching the maximum stimulating value (4095). A calibration step is then require here.

    Trimmer potentiometers corresponding to each LED channels can be found on the device. They regulate the maximum current intensity each stimulating LED can be drove with.

    First, user need to set each stimulating LED to their desired maximum intensity by adjusting the potentiometer value.

    Once done, play a <a href="">step-increased stimulation sequence</a> for the tested LED and not at which value the LED maximum intensity is reached and (may?) plateau.

    Finally enter the noted value in the <strong> LED_Values.h</strong> tab.
    

    <br></br>

    Reupload the code onto the board, now the tested LED will have a linear intensity increase from 0 to 100% without any saturation.

<br></br>

No further modification of the code is then required from the user who can now control the board directly from the GUI.

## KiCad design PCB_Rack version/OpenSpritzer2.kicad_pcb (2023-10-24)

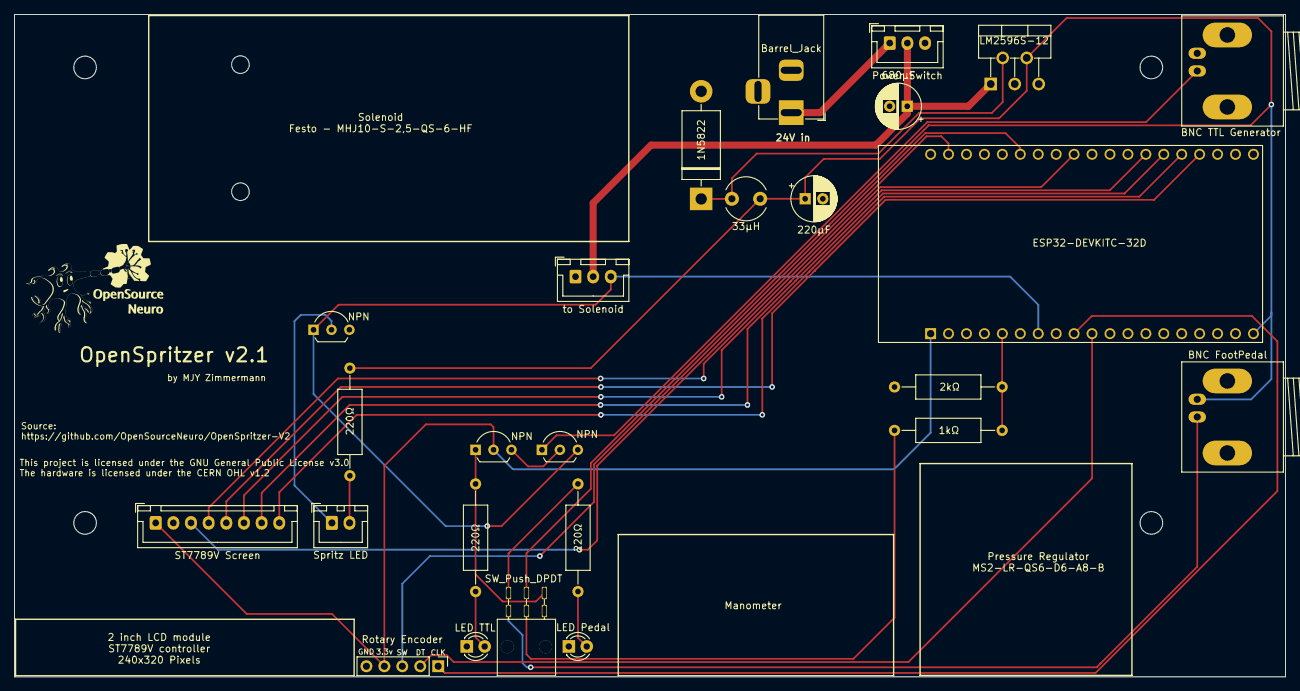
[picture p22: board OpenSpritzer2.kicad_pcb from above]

Board: 2 copper layers, 180.0 x 93.8 mm, 25 parts (0 on the bottom side), 27 nets.

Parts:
C1: 680μF; CP_Radial_D6.3mm_P2.50mm
C2: 220μF; CP_Radial_D6.3mm_P2.50mm
D1: 1N5822; D_DO-201AD_P15.24mm_Horizontal
D2: LED Pedal; LED_D3.0mm
D3: LED TTL; LED_D3.0mm
D4: Spritz LED; JST_XH_B2B-XH-A_1x02_P2.50mm_Vertical
J1: Barrel_Jack; BarrelJack_Horizontal
J2: BNC FootPedal; BNC_Socket_TYCO-AMP_LargePads
J3: BNC TTL Generator; BNC_Socket_TYCO-AMP_LargePads
J4: to Solenoid; JST_XH_B3B-XH-A_1x03_P2.50mm_Vertical
L1: 33μH; L_Radial_D6.0mm_P4.00mm
NPN: NPN; TO-92L_Inline_Wide
NPN#2, NPN#3: NPN; TO-92L_Inline_Wide
R1, R2, R5: 220Ω; R_Axial_DIN0309_L9.0mm_D3.2mm_P15.24mm_Horizontal
R3: 1kΩ; R_Axial_DIN0309_L9.0mm_D3.2mm_P15.24mm_Horizontal
R4: 2kΩ; R_Axial_DIN0309_L9.0mm_D3.2mm_P15.24mm_Horizontal
SW1: Power Switch; JST_XH_B3B-XH-A_1x03_P2.50mm_Vertical
SW2: SW_Push_DPDT; maxi_DPDT_Angled
SW3: Rotary Encoder; PinHeader_1x05_P2.54mm_Vertical
U1: ESP32-DEVKITC-32D; MODULE_ESP32-DEVKITC-32D
U2: LM2596S-12; TO-220-5_P3.4x3.7mm_StaggerOdd_Lead3.8mm_Vertical
U3: ST7789V Screen; JST_XH_B8B-XH-A_1x08_P2.50mm_Vertical

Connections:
3.3V: NPN#2.2 (C), SW3.4 (S1), U1.1 (3V3), U3.1 (VCC)
GNDREF: C1.2, C2.2, D1.2 (A), D2.1 (K), D3.1 (K), J1.2, J1.3, J2.2 (Ext), J3.2 (Ext), J4.1, NPN#3.3 (E), R4.1, SW1.3 (K), SW3.5 (S2), U1.14 (GND1), U1.20 (GND3), U1.26 (GND2), U2.3 (GND), U2.5 (~ON/OFF), U3.2 (GND)
GPIO0: U1.33 (IO0), U3.7 (RST)
GPIO2: U1.34 (IO2), U3.8 (BL)
GPIO4: U1.32 (IO4), U3.6 (DC)
GPIO15: U1.35 (IO15), U3.5 (CS)
GPIO18: U1.28 (IO18), U3.4 (CLK)
GPIO21: SW3.3 (B), U1.25 (IO21)
GPIO23: U1.21 (IO23), U3.3 (DIN)
GPIO25: SW3.1 (A), U1.9 (IO25)
GPIO26: SW3.2 (C), U1.10 (IO26)
GPIO32: J4.3, NPN.3 (E), NPN#3.1 (B), U1.7 (IO32)
GPIO34: R3.2, R4.2, U1.5 (IO34)
unnamed: D1.1 (K), L1.1, U2.2 (OUT)
unnamed: D2.2 (A), R1.1
unnamed: D3.2 (A), R2.1
unnamed: D4.1 (K), NPN#3.2 (C)
unnamed: D4.2 (A), R5.1
unnamed: J1.1, SW1.1
unnamed: J3.1 (In), NPN.1 (B)
unnamed: NPN.2 (C), NPN#2.3 (E)
unnamed: R1.2, SW2.1 (A)
unnamed: NPN#2.1 (B), R2.2, SW2.3 (C)
unnamed: R3.1, SW2.5 (B)
unnamed: J2.1 (In), SW2.4 (A)
VCC 5V: C2.1, J2.2 (Ext), L1.2, R5.2, SW2.2 (B), U1.19 (EXT_5V), U2.4 (FB)
Vin 24V: C1.1, J4.2, SW1.2 (A), U2.1 (VIN)

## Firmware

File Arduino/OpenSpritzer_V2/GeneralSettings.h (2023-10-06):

#include <PNGdec.h>
#include <SPI.h>
#include <Wire.h>
#include <Adafruit_GFX.h>

#include "WelcomeScreen.h"
#include "AiEsp32RotaryEncoder.h"
#include "AiEsp32RotaryEncoderNumberSelector.h"
#include "Menus.h"

bool Flag_Menu;
bool Flag_MenuSelection;
bool menu_select;
bool menu_select_close;

#define Solenoid      32
#define Pedal         34
#define SpritzLED     5

#define Rotary_SW     21
#define Rotary_DT     26
#define Rotary_CLK    25
#define Rotary_VCC    -1 
#define Rotary_Steps   4

AiEsp32RotaryEncoder *rotaryEncoder = new AiEsp32RotaryEncoder(Rotary_DT, Rotary_CLK, Rotary_SW, Rotary_VCC, Rotary_Steps);
AiEsp32RotaryEncoderNumberSelector numberSelector = AiEsp32RotaryEncoderNumberSelector();

unsigned long RotaryAcceleration = 250;
int RotaryMinimum                = 0;
int RotaryMaximum                = 999999;
static unsigned long RotaryTime;
unsigned long RotaryDuration     = 10000;
void IRAM_ATTR readEncoderISR(){
    rotaryEncoder->readEncoder_ISR();
}



void HardwareSettings(){

    tft.setRotation(3);

    TitleFlag = true;

    Flag_Menu = false;
    Flag_MenuSelection = false;
    Flag_MenuSelected = false;

    menu1_selected = false;
    menu2_selected = false;
    menu3_selected = false;
    menu_select = false;
    menu_select_close = false;

    rotaryEncoder->begin();
    rotaryEncoder->setup(readEncoderISR);
    numberSelector.attachEncoder(rotaryEncoder);

    pinMode(Pedal, INPUT);
    pinMode(Solenoid, OUTPUT);
    pinMode(SpritzLED, OUTPUT);

    digitalWrite(Solenoid, LOW);  
    digitalWrite(SpritzLED, LOW);
}




void Menu_Loop(){

  numberSelector.setRange(0, 2, 1, true, 0);
  numberSelector.setValue(0);
  rotaryEncoder->setAcceleration(0);
  MenuSelection = 0;
  Flag_Menu = true;
  Flag_MenuSelection = true;
  FirstMenuSelected();
}


void Menu_Selection(){

  MenuSelection = numberSelector.getValue();
  
  if (MenuSelection == 0 && Flag_MenuSelected == true){
    FirstMenuSelected();
  }
  if (MenuSelection == 1 && Flag_MenuSelected == true){
    SecondMenuSelected();
  }
  if (MenuSelection == 2 && Flag_MenuSelected == true){
    ThirdMenuSelected();    
  }
}


void MenuSelection_Loop_Close(){

  if (MenuSelection == 0){
    menu1_selected = false;
    menu_select = false;
    menu_select_close = false;
    FirstMenuSelected();
    numberSelector.setRange(0, 2, 1, true, 0);
    numberSelector.setValue(MenuSelection);
    rotaryEncoder->setAcceleration(0);
  }

  if (MenuSelection == 1){
    menu2_selected = false;
    menu_select = false;
    menu_select_close = false;
    SecondMenuSelected();
    numberSelector.setRange(0, 2, 1, true, 0);
    numberSelector.setValue(MenuSelection);
    rotaryEncoder->setAcceleration(0);
  }

  if (MenuSelection == 2){
    menu3_selected = false;
    menu_select = false;
    menu_select_close = false;
    ThirdMenuSelected();
    numberSelector.setRange(0, 2, 1, true, 0);
    numberSelector.setValue(MenuSelection);
    rotaryEncoder->setAcceleration(0);
  }
}


void MenuSelection_Loop_Open(){

  if (MenuSelection == 0){
    menu1_selected = true;
    menu_select_close = true;
    FirstMenuSelectedText();
    numberSelector.setRange(1, 100, 1, false, 0);
    numberSelector.setValue(NumberOfPulse);
    rotaryEncoder->setAcceleration(0);
  }

  if (MenuSelection == 1){
    menu2_selected = true;
    menu_select_close = true;
    SecondMenuSelectedText();
    numberSelector.setRange(RotaryMinimum, RotaryMaximum, 1, false, 0);
    numberSelector.setValue(PulseOn);
    rotaryEncoder->setAcceleration(RotaryAcceleration);  
  }

  if (MenuSelection == 2){
    menu3_selected = true;
    menu_select_close = true;
    ThirdMenuSelectedText();
    
    numberSelector.setRange(RotaryMinimum, RotaryMaximum, 1, false, 0);
    numberSelector.setValue(PulseOff);
    rotaryEncoder->setAcceleration(RotaryAcceleration);  
  }

}

void NumberOfPulse_Loop(){
  NumberOfPulse = numberSelector.getValue();
  FirstMenuSelectedText();
}

void PulseOn_Loop(){
  PulseOn = numberSelector.getValue();
  SecondMenuSelectedText();
}

void PulseOff_Loop(){
  PulseOff = numberSelector.getValue();
  ThirdMenuSelectedText();
}

void Refresh(){
  RotaryTime = 0;
  Flag_Menu = false;
  HomePage();
}

void Pulse(){
  for (int i = 1; i <= NumberOfPulse; i++){
    digitalWrite(Solenoid, HIGH);
    digitalWrite(SpritzLED, HIGH);
    delay(PulseOn);
    digitalWrite(Solenoid, LOW);
    digitalWrite(SpritzLED, LOW);
    delay(PulseOff);
  }
}

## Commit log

2023-10-06 Upload Arduino
2023-10-06 Upload Casing
    [OPenSpritzer2.scad, back.dxf, bottom.dxf, front.dxf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]
2023-10-06 Upload PCB
    [OpenSpritzer2-B_Cu.gbr, OpenSpritzer2-B_Mask.gbr, OpenSpritzer2-B_Paste.gbr, OpenSpritzer2-B_Silkscreen.gbr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]
2023-10-24 update pcb
    [OpenSpritzer2-B_Cu.gbr, OpenSpritzer2-B_Mask.gbr, OpenSpritzer2-B_Paste.gbr, OpenSpritzer2-B_Silkscreen.gbr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]
2024-01-01 update casing
    [OpenSpritzer_v2.scad, back.dxf, bottom.dxf, front.dxf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]
2024-01-06 create Arduino libraires

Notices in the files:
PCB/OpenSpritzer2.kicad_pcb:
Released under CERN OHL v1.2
